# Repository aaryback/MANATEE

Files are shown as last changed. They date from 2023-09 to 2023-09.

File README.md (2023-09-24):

# "DIY" Emulsions using MANATEE (MANifold Adapter and Tray for Easy Emulsions)
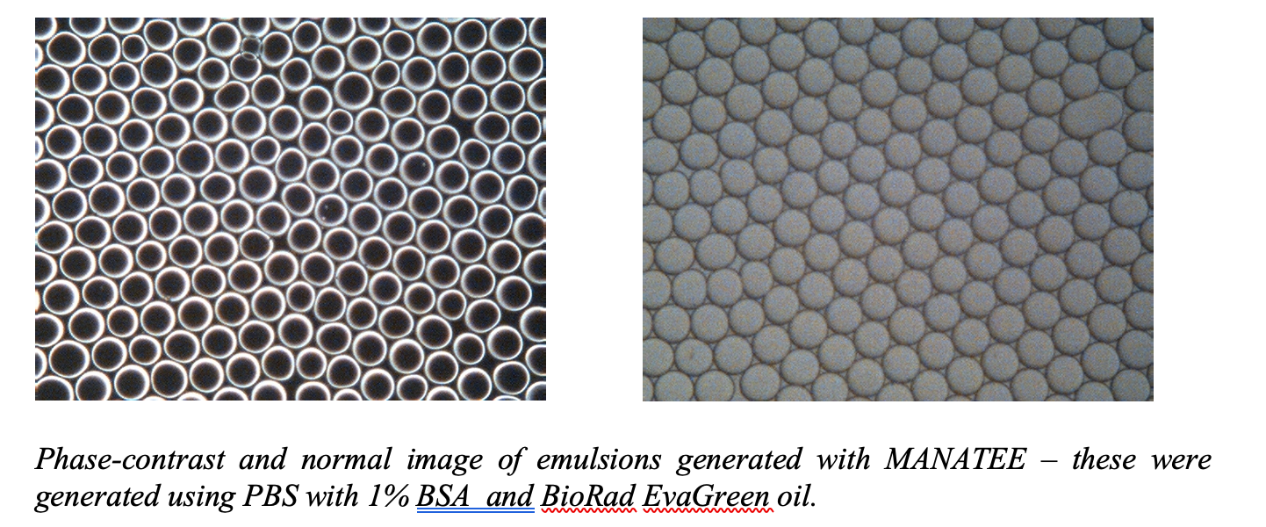
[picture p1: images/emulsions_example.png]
Example Emulsions


Here are instructions for making uniform emulsions using a 3D printed manifold attached to a generic vacuum source and a simple Arduino-controlled vacuum release system. 

The system uses commercially available QX200 microfluidics chips from BioRad QX200™ Droplet Digital™ PCR System and rubber gaskets, and the EvaGreen Droplet Generation Oil. It can save you buying the droplet generator if you want to just make emulsions - we weren’t interested in using it for digital droplet PCR so did not need the droplet reader either. This design could definitely be refined and improved, but as it stands it works just fine to make stable emulsions! If you have a very sensitive vacuum pump that can operate in the 5-15kPa range, then you can just attach that straight to the MANATEE and make your emulsions. We didn’t have that available, so instead made a ‘vacuum release’ circuit which can be attached to a generic vacuum source and then just releases the low level of vacuum needed to generate the emulsions.

## The MANATEE

The MANATEE manifold and tray were 3D printed using SLS with plastic polyamide 11: PA 11 plastic. 3D objects were uploaded to [Shapeways](https://www.shapeways.com/). and ordered for 3D printing. See “3D_objects” folder for the 3D printing files. SLS was chosen since extrusion-based 3D printing tends to have a slightly ribbed/uneven surface and to allow the wells on the microfluidics chip to be completely sealed off I wanted a super smooth finish. The tray could be printed using standard extrusion-based 3D printing though since its function is mainly to keep the rubber gasket and the microfluidics chip secured. The MANATEE was designed so that the Manifold can be clamped onto the tray with a vice (or similar) and even pressure applied.

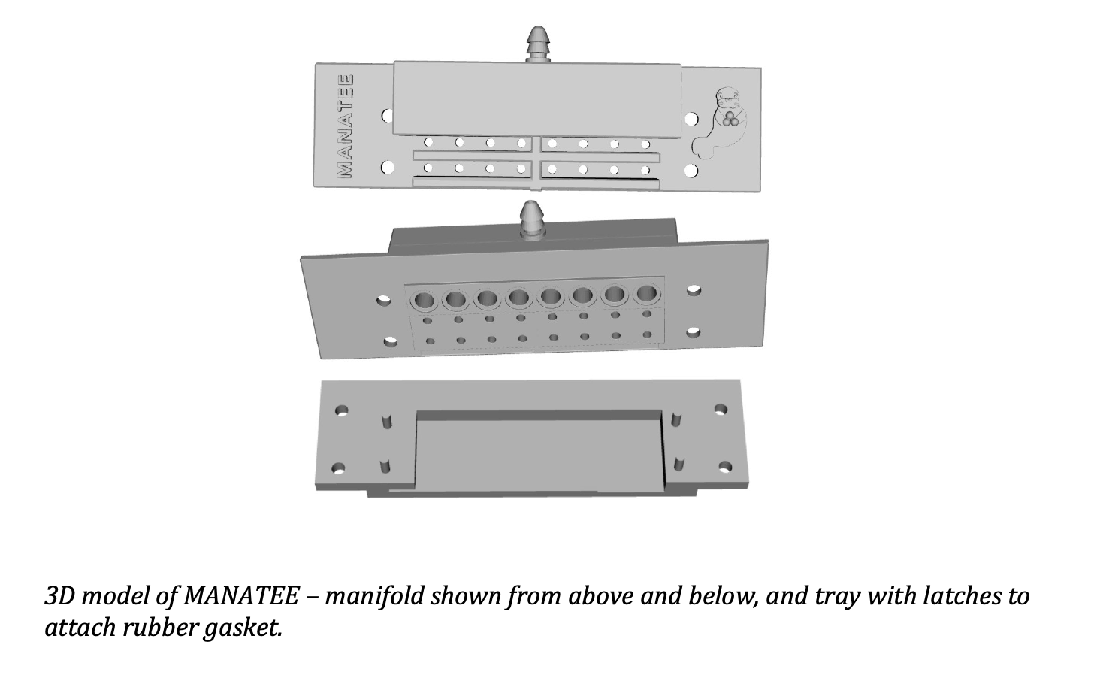
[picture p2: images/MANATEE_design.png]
MANATEE 3D design


3D model of MANATEE – manifold shown from above and below, and tray with latches to attach rubber gasket.

The microfluidics chip only slots into the tray in one orientation. The oil is added to the bottom well, the mastermix to the middle well and the emulsion is collected from the top well. The gasket is the strapped over the chip on the tray, fitting the holes on either end of the gasket over the latches. Then use a vice or similar to secure the manifold to the tray. I clamp both onto the workbench to ensure it is tightly sealed and no air enters the manifold while the droplets are being generated. Apply a vacuum (I’ve found 6-10kPa is generally the range needed for most PCR reagents, but it will depend on the viscosity of the aqueous solution) until all the oil is drawn through the chip. You can see the level of oil left within the wells, looking at the manifold side-on.

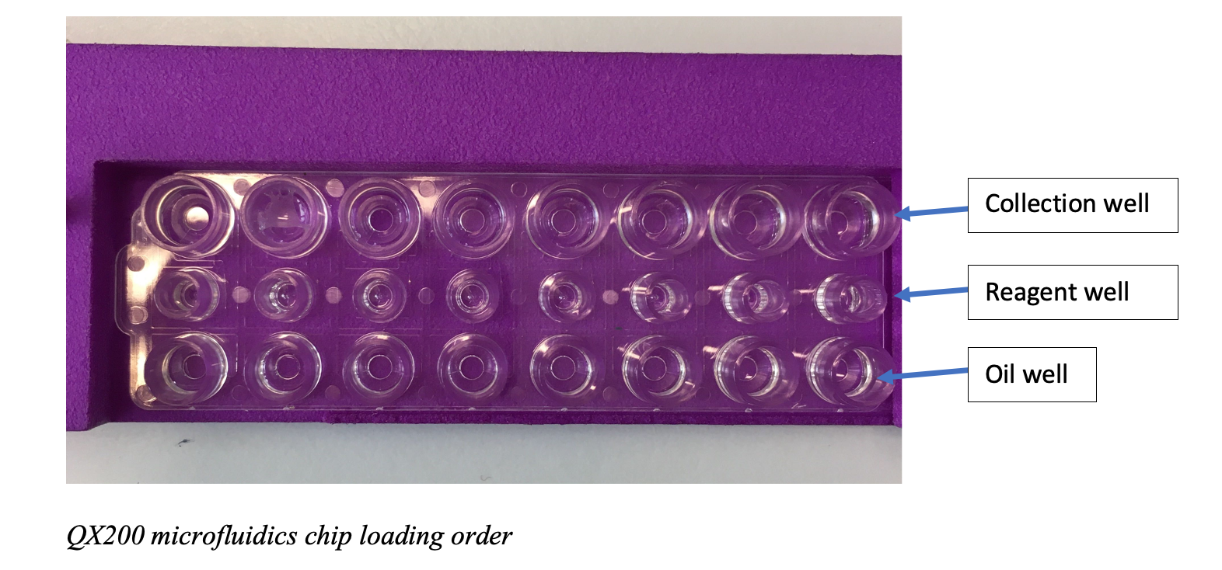
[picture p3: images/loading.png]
loading microfludics chip


## Vacuum Release System

If, like me, you don’t have access to a vacuum pump that can apply very low levels of vacuum required for microfluidics, you can also build this vacuum release system. When looking for precision vacuum pumps (that we were allowed to buy via the university) I was looking at having to spend several thousand pounds. So instead I just thought I’d use our existing crude vacuum pumps (e.g. ELISA plate washer) and release vacuum from there in a controlled manner. The whole thing probably cost around £50 to make (including the Arduino and tubing etc.), although I did already have some of the components (like the Duran bottle and ports for the Duran Bottle lid and some of the tubing). The expensive components are the Arduino and the pressure gauge. This circuit could be moved onto one of the really small Arduino circuit boards since you only need one digital and one analogue pin. The image below displays the overview of the main components in the setup:

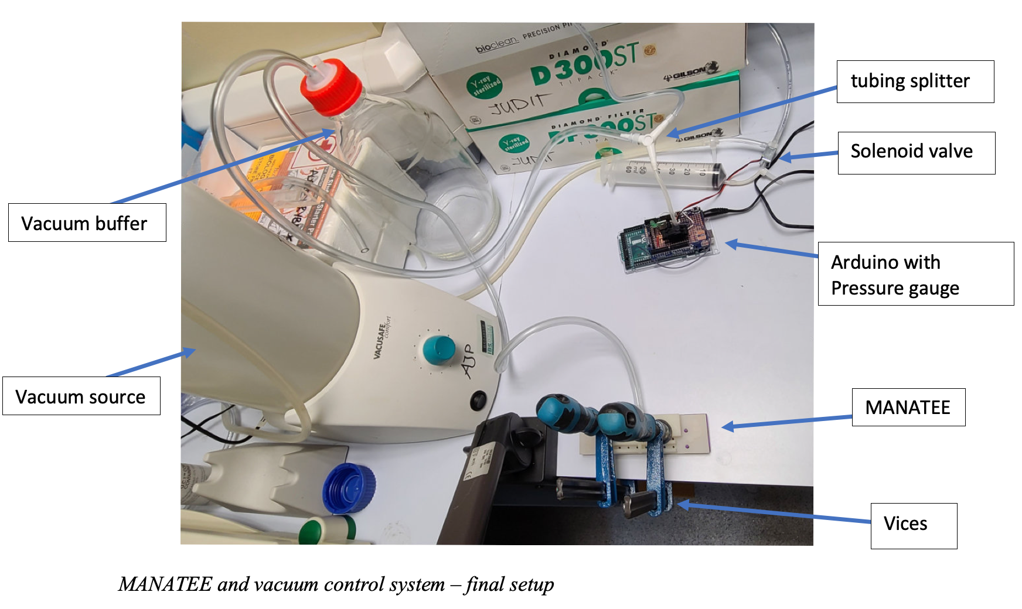
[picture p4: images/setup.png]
Droplet Generation Setup


Basically, the pressure gauge measures the vacuum in the system and if it is below the desired threshold, it briefly opens the solenoid valve to let more vacuum into the manifold, before closing off again. The circuit keeps opening and closing the solenoid valve to keep it roughly around the desired vacuum threshold. An LED light blinks each time more vacuum is released into the manifold, and as a way of making sure the circuit is working.

### A Brief Note on the Solenoid Valve:

I used a solenoid air valve, after considering quite a few different options this was the cheapest and simplest I could find (<£3). It can also easily be replaced since it plugs into the circuit rather than being soldered in. However, it does have three ports and switches between the central port (Port A) opening towards the lower plastic port (Port B), and the upper metal port (Port C). Because of this, I sealed Port B off so that vacuum accumulates in the plate-washer pump / tubing which is then released into the manifold. In the images, I just connected port B to a syringe with some tubing because this was the easiest “stopper” available to me but anything would work.

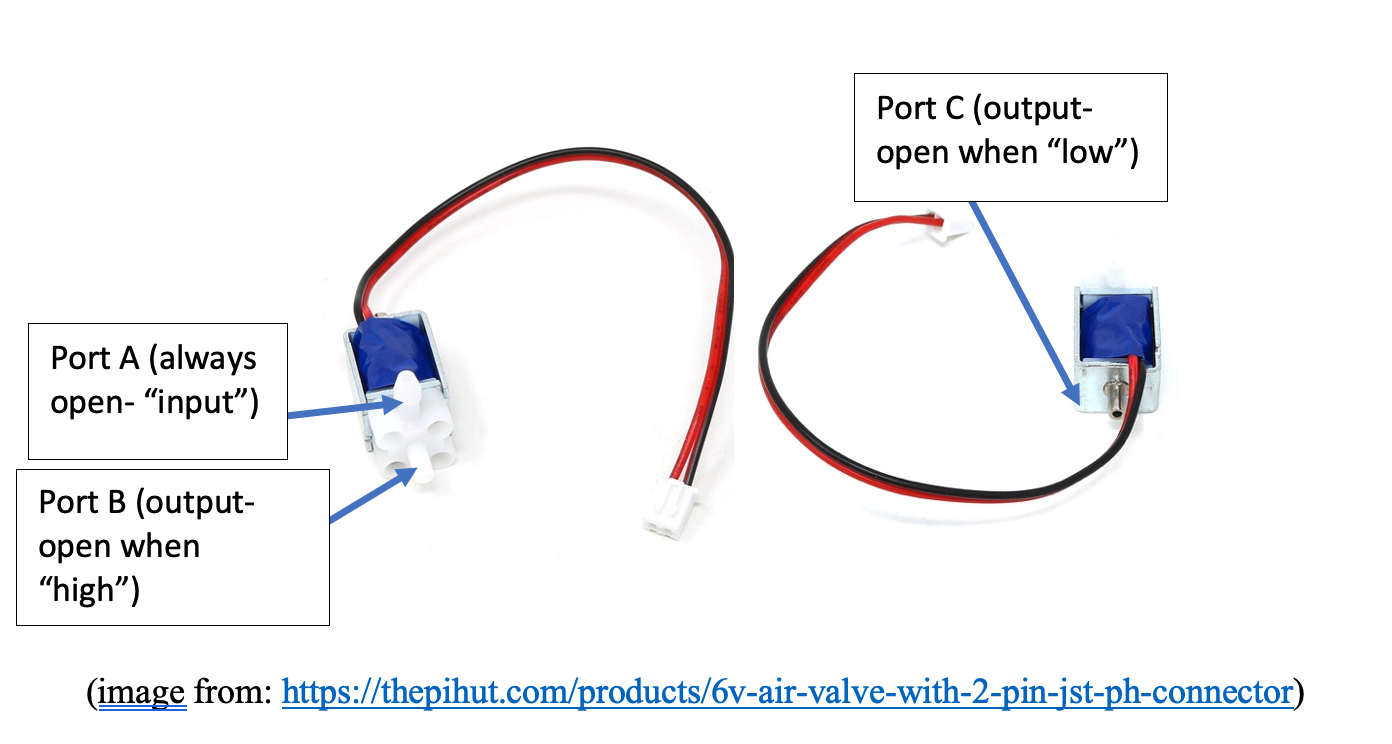
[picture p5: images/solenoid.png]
Solenoid valve


### Wiring up the Circuit:

Here are the details for the circuit (shown on a breadboard – in the final version this was soldered to an Arduino prototyping board):

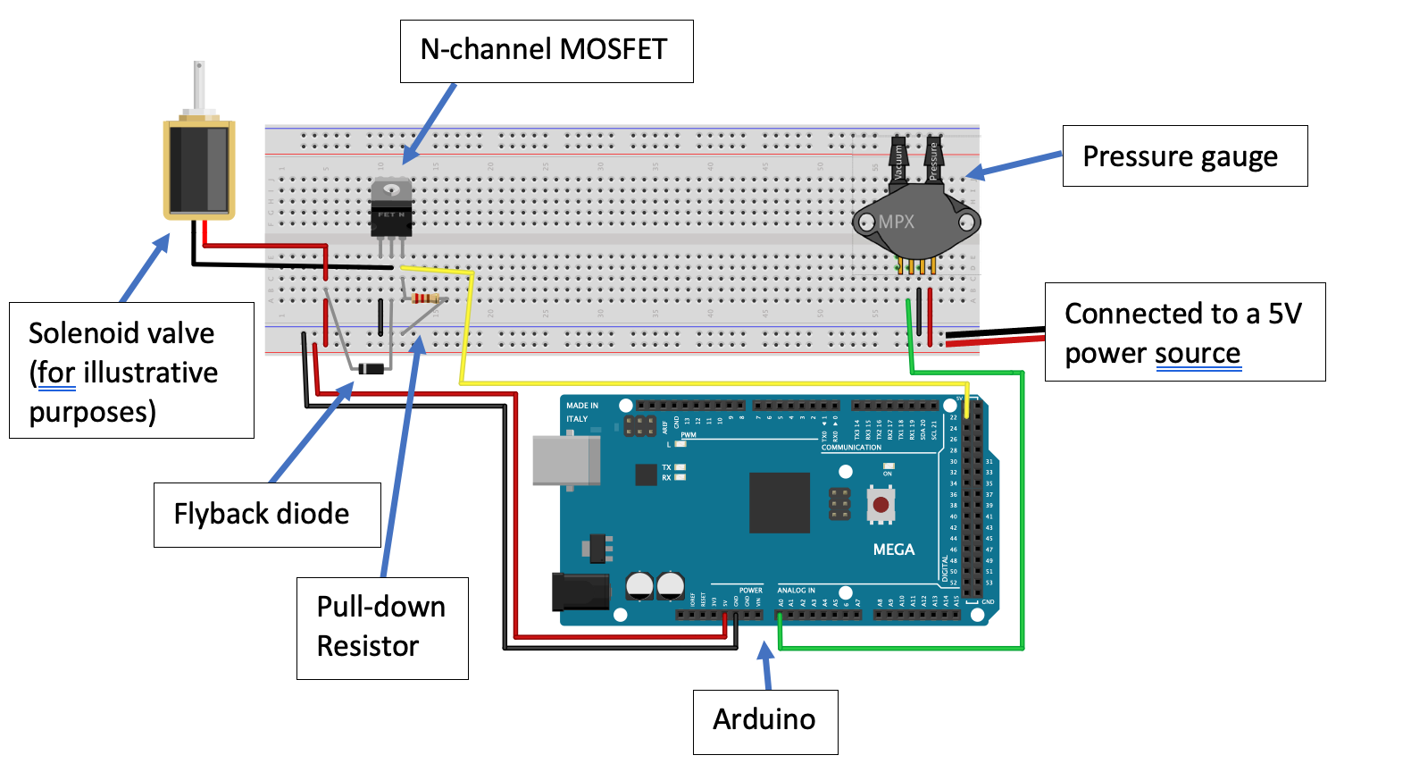
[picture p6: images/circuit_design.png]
Circuit


There are two main parts of the circuit: the pressure gauge and the solenoid. The pressure gauge is very simple:

I used an MPX5100 DP – a dual port differential pressure sensor (unlike the diagram it actually has 6 pins, but as in the diagram above, only the first three pins are used) which measures the difference in pressure between the two ports- one exposed to atmospheric pressure and the other one connected to the MANATEE.

In brief, the MPX5100 DP pressure gauge is connected to an Analog input pin on the Arduino (A0 here) and it is connected to power and ground. Code for pressure gauge was adapted from [here](https://circuits4you.com/2016/05/13/arduino-pressure-measurement/). As a quick sanity check that the calibration was correct, I checked the calibrated pressure against the observed output voltage and compared that to the manufacturer’s datasheet.

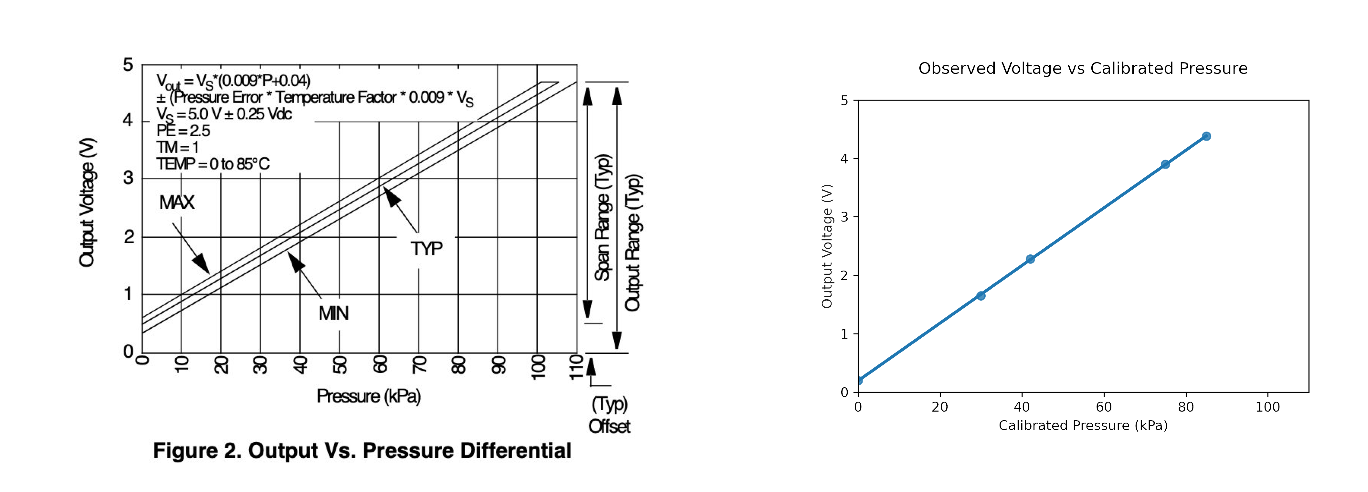
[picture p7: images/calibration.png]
Calibrating Pressure Gauge


Powering of the solenoid valve is controlled by a MOSFET, which in turn is controlled by the Arduino. The solenoid valve is connected to power directly but ground is connected to the middle pin of the N-Channel MOSFET. Pin 1 of the MOSFET connects to ground, pin 2 is the “output” connected to the solenoid and pin 3 is connected to the Arduino and to ground via a 220 ohm pull-down resistor. When the MOSFET receives a “HIGH” signal from the Arduino it opens the channel and powers the solenoid on, which blocks the airflow between the vacuum source and the MANATEE. When the MOSFET receives a “LOW” signal from the Arduino it powers the solenoid off and opens the airflow between the vacuum source and the MANATEE. A Flyback diode is included between the power and ground of the solenoid. If you want to include an LED to visually show whether the solenoid is powered on or off, you can include that between pin 3 of the MOSFET and the Digital pin 22 on the Arduino. 

The final Arduino code can be found in the folder [Arduino_Code](./Arduino_Code).

### Connecting the tubes:

I connected the tubing as follows: The vacuum source was connected to Port A of the solenoid valve. Port B of the solenoid is sealed off and not used. Port C of the solenoid valve feeds into a three way tube splitter with one port leading to a large Duran bottle to buffer the vacuum which also leads to the MANATEE, and the other port leading to the vacuum sensing port of the dual-port pressure gauge. This allows the vacuum in the manifold to be measured. 
To operate it, first turn on the vacuum release circuit, then the vacuum source.
Finally, it is worth mentioning that this system is pretty flexible: I’ve tried BioRad’s RT-PCR reagents and Roche Titan’s RT-PCR mastermix (with BSA added!) and gotten thermostable emulsions. Other PCR reagents work too, just titrate BSA and surfactant (I used a non-ionic plurionic surfactant) and try a range of vacuum levels. Some commercial PCR reagents produce emulsions that look OK initially but go “sticky” once thermocycled. I don’t know what additives in the mastermix make this happen, but I’d just recommend trying them out empirically and seeing what works.

| Part                       | Catalogue Numbers / Specifications                                   |
|----------------------------|---------------------------------------------------------------------|
| Arduino                    | Arduino Mega 2560                                                  |
| Pressure Gauge              | MPX5100DP                                                           |
| Solenoid Valve              | DFRobot 6V 2-Position 3-Way Air Valve for Arduino (DFR0866)        |
| N-channel Power MOSFET     | IRLB8721PbF                                                         |
| Flyback Diode              | Vishay (1N4007E354)                                                |
| Green LED                  | Kingbright2 V Green LED 5mm (L-53GD, RS Components)                |
| Resistors                  | 220 Ω Resistor (RS PRO)                                            |
| Prototyping PCB Board      | Arduino UNO R3 ProtoShield (483150)                                 |
| Plastic PVC Tubing         | - RS PRO Hose Pipe, PVC, 3mm ID, 6mm OD                            |
|                            | - 2.5mm inner diameter stretchable tubing (use tubing 2.5-3mm wide, depending on how you connect your vacuum source) |
| Y-tubing Splitter          | I used one compatible with tubes 2-6mm in diameter. This was quite helpful as I could stretch different sized tubes onto the same splitter. |
| Sealing Grease             |                                                                     |
| Cable Ties                 |                                                                     |

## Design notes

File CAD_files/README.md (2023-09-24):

This folder contains the CAD files for 3D printing the MANATEE Manifold and Tray. I've uploaded both the designs as ".stl" files. You can also find the design and project description on "Thingiverse" [here](https://www.thingiverse.com/thing:6174004).

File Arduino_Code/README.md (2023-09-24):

This Arduino code runs the pressure gauge code and solenoid. Sensor offset may need to be adjusted depending on your Arduino.

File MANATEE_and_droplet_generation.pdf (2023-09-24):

Audrey Ryback – August 2023

Home-made emulsions using MANATEE (MANifold Adapter and Tray for Easy Emulsions):

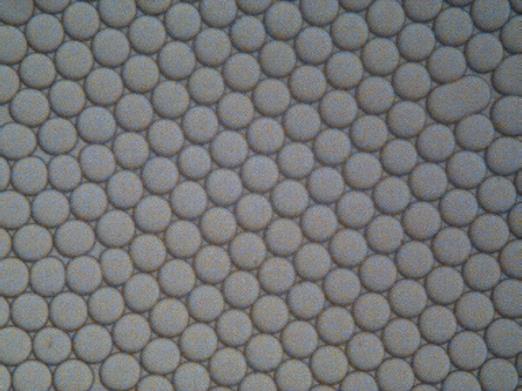
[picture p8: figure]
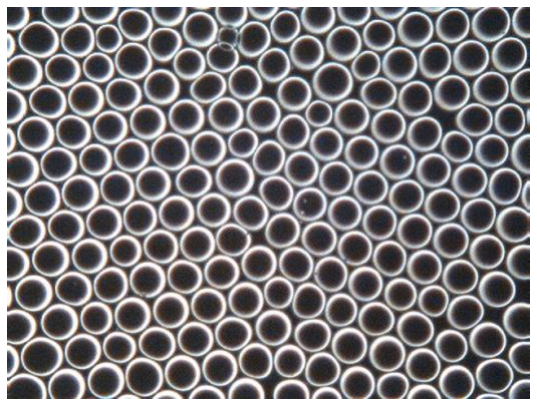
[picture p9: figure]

Phase-contrast and normal image of emulsions generated with MANATEE – these were generated using PBS with 1% BSA and BioRad EvaGreen oil.

Here are instructions for making uniform emulsions using a 3D printed manifold attached to a generic vacuum source and a simple Arduino-controlled vacuum release system. The system uses commercially available QX200 microfluidics chips from BioRad QX200™ Droplet Digital™ PCR System and rubber gaskets, and the EvaGreen Droplet Generation Oil. It can save you buying the droplet generator if you want to just make emulsions - we weren’t interested in using it for digital droplet PCR so did not need the droplet reader either. This design could definitely be refined and improved, but as it stands it works just fine to make stable emulsions! If you have a very sensitive vacuum pump that can operate in the 5-15kPa range, then you can just attach that straight to the MANATEE and make your emulsions. We didn’t have that available, so instead made a ‘vacuum release’ circuit which can be attached to a generic vacuum source and then just releases the low level of vacuum needed to generate the emulsions.

The MANATEE

The MANATEE manifold and tray were 3D printed using SLS with plastic polyamide 11: PA 11 plastic. 3D objects were uploaded to Shapeways (https://www.shapeways.com/) and ordered for 3D printing. See “3D_objects” folder for the 3D printing files. SLS was chosen since extrusion-based 3D printing tends to have a slightly ribbed/uneven surface and to allow the wells on the microfluidics chip to be completely sealed off I wanted a super smooth finish. The tray could be printed using standard extrusion-based 3D printing though since its function is mainly to keep the rubber gasket and the microfluidics chip secured. The MANATEE was designed so that the Manifold can be clamped onto the tray with a vice (or similar) and even pressure applied.

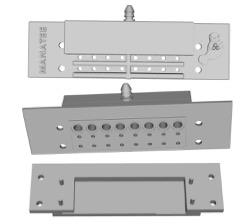
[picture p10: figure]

3D model of MANATEE – manifold shown from above and below, and tray with latches to attach rubber gasket.

The microfluidics chip only slots into the tray in one orientation. The oil is added to the bottom well, the mastermix to the middle well and the emulsion is collected from the top well.

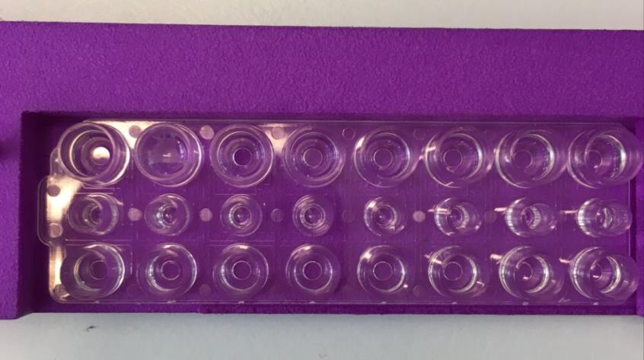
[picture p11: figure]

QX200 microfluidics chip loading order

The gasket is the strapped over the chip on the tray, fitting the holes on either end of the gasket over the latches.

Then use a vice or similar to secure the manifold to the tray. I clamp both onto the workbench to ensure it is tightly sealed and no air enters the manifold while the droplets are being generated. Apply a vacuum (I’ve found 6-10kPa is generally the range needed for most PCR

Oil well

Reagent well

Collection well reagents, but it will depend on the viscosity of the aqueous solution) until all the oil is drawn through the chip. You can see the level of oil left within the wells, looking at the manifold side-on.

Vacuum release system

If, like me, you don’t have access to a vacuum pump that can apply very low levels of vacuum required for microfluidics, you can also build this vacuum release system. When looking for precision vacuum pumps (that we were allowed to buy via the university) I was looking at having to spend several thousand pounds. So instead I just thought I’d use our existing crude vacuum pumps (e.g. ELISA plate washer) and release vacuum from there in a controlled manner. The whole thing probably cost around £50 to make (including the Arduino and tubing etc.), although I did already have some of the components (like the Duran bottle and ports for the Duran Bottle lid and some of the tubing). The expensive components are the Arduino and the pressure gauge. This circuit could be moved onto one of the really small Arduino circuit boards since you only need one digital and one analogue pin. The image below displays the overview of the main components in the setup:

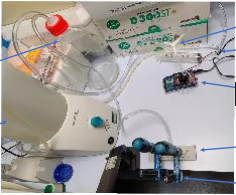
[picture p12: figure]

MANATEE and vacuum control system – final setup

Basically, the pressure gauge measures the vacuum in the system and if it is below the desired threshold, it briefly opens the solenoid valve to let more vacuum into the manifold, before closing off again. The circuit keeps opening and closing the solenoid valve to keep it roughly around the desired vacuum threshold. An LED light blinks each time more vacuum is released into the manifold, and as a way of making sure the circuit is working.

Arduino with
Pressure gauge

MANATEE

Vices

Vacuum source

Vacuum buffer

Solenoid valve

tubing splitter

A brief note on the solenoid valve:

I used a solenoid air valve, after considering quite a few different options this was the cheapest and simplest I could find (<£3). It can also easily be replaced since it plugs into the circuit rather than being soldered in. However, it does have three ports and switches between the central port (Port A) opening towards the lower plastic port (Port B), and the upper metal port (Port C). Because of this, I sealed Port B off so that vacuum accumulates in the plate-washer pump / tubing which is then released into the manifold. In the images, I just connected port B to a syringe with some tubing because this was the easiest “stopper” available to me but anything would work.

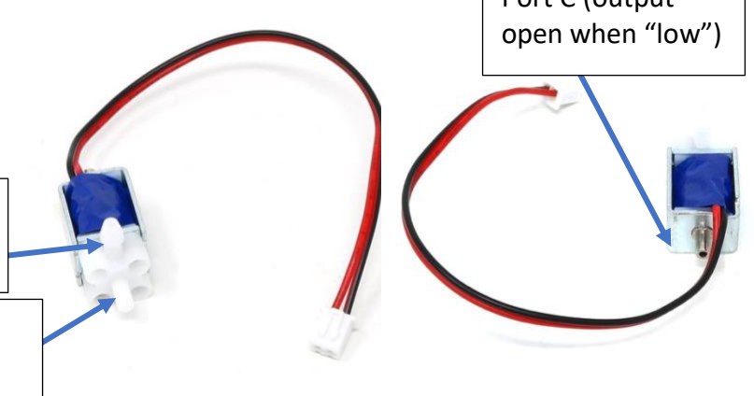
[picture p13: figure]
open when “low”)

(image from: https://thepihut.com/products/6v-air-valve-with-2-pin-jst-ph-connector)

Port A (always
open- “input”)

Port B (output-open when
“high”)

Port C (output-

Wiring up the circuit

Here are the details for the circuit (shown on a breadboard – in the final version this was soldered to an Arduino prototyping board):

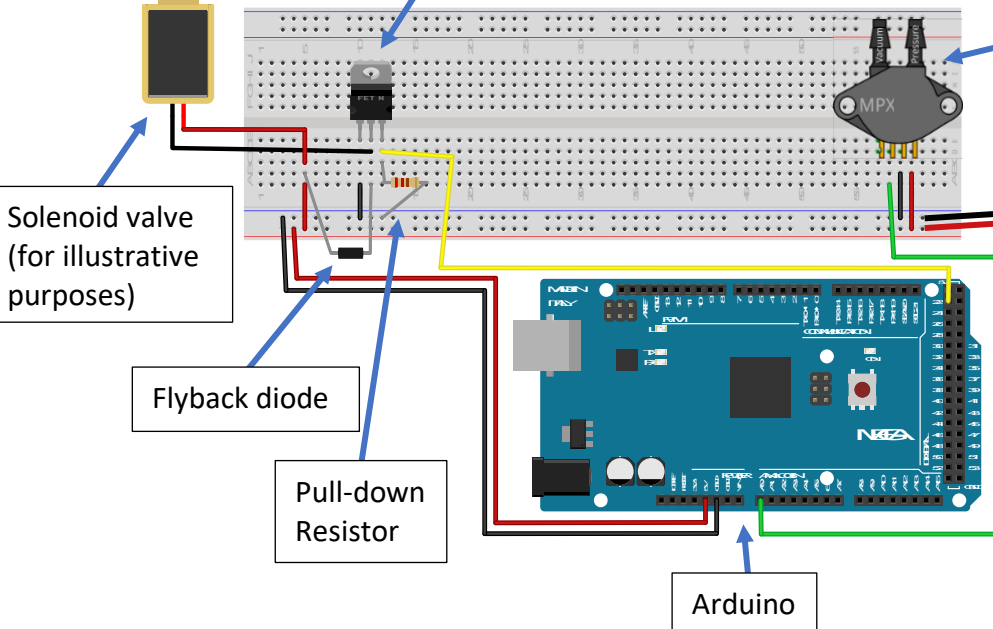
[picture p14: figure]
ANALOGIN; COMUNICATION; POWER; AREF; GND; RESET; VIN; SDA20; SCL21; MADEIN; ITALY; PWM; DIGITA; MEGA L; IOREF; Solenoid valve (for illustrative purposes); Flyback diode; Pull-down Resistor; Arduino

There are two main parts of the circuit: the pressure gauge and the solenoid. The pressure gauge is very simple:
I used an MPX5100 DP – a dual port differential pressure sensor (unlike the diagram it actually has 6 pins, but as in the diagram above, only the first three pins are used) which measures the difference in pressure between the two ports- on exposed to atmospheric pressure and the other one connected to the MANATEE.

In brief the MPX5100 DP pressure gauge is connected to an Anolog input pin on the Arduino (A0 here) and it is connected to power and ground. Code for pressure gauge was adapted from here: https://circuits4you.com/2016/05/13/arduino-pressure-measurement/ . As a quick sanity check that the calibration was correct, I checked the calibrated pressure against the observed output voltage and compared that to the manufacturer’s datasheet.

Pressure gauge

N-channel MOSFET

Connected to a 5V
power source

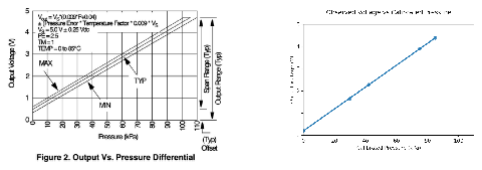
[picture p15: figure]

Powering of the solenoid valve is controlled by a MOSFET, which in turn is controlled by the Arduino. The solenoid valve is connected to power directly but ground is connected to the middle pin of the N-Channel MOSFET. Pin 1 of the MOSFET connects to ground, pin 2 is the “output” connected to the solenoid and pin 3 is connected to the Arduino and to ground via a 220 ohm pull-down resistor. When the MOSFET receives a “HIGH” signal from the Arduino it opens the channel and powers the solenoid on, which blocks the airflow between the vacuum source and the MANATEE. When the MOSFET receives a “LOW” signal from the Arduino it powers the solenoid off and opens the airflow between the vacuum source and the MANATEE. A Flyback diode is included between the power and ground of the solenoid. If you want to include an LED to visually show whether the solenoid is powered on or off, you can include that between pin 3 of the MOSFET and the Digital pin 22 on the Arduino.

The final Arduino code can be found in the folder “Arduino_code”.

Connecting the tubes:

I connected the tubing as follows: The vacuum source was connected to Port A of the solenoid valve. Port B of the solenoid is sealed off and not used. Port C of the solenoid valve feeds into a three way tube splitter with one port leading to a large Duran bottle to buffer the vacuum which also leads to the MANATEE, and the other port leading to the vacuum sensing port of the dual-port pressure gauge. This allows the vacuum in the manifold to be measured.

To operate it, first turn on the vacuum release circuit, then the vacuum source.

Finally, it is worth mentioning that this system is pretty flexible: I’ve tried BioRad’s RT-PCR reagents and Roche Titan’s RT-PCR mastermix (with BSA added!) and gotten thermostable emulsions. Other PCR reagents work too, just titrate BSA and surfactant (I used a non-ionic plurionic surfactant) and try a range of vacuum levels. Some commercial PCR reagents produce emulsions that look OK initially but go “sticky” once thermocycled. I don’t know what additives in the mastermix make this happen, but I’d just recommend trying them out empirically and seeing what works.

Materials:

Part | Catalogue Numbers / specifications
Arduino | Arduino Mega 2560
Pressure Gage | MPX5100DP
Solenoid Valve | DFRobot 6V 2-Position 3-Way Air Valve for Arduino (DFR0866)
N channel power MOSFET (30V 60A) | IRLB8721PbF
Flyback diode | Vishay (1N4007E354)
Green LED | Kingbright2 V Green LED 5mm (L-53GD, RS components)
Resistors | 220 Ω Resistor (RS PRO
Prototyping PCB board | Arduino UNO R3 ProtoShield (483150)
Plastic PVC tubing | - RS PRO Hose Pipe, PVC, 3mm ID, 6mm OD - 2.5mm inner diameter stretchable tubing (use tubing 2.5-3mm wide, depending on how you connect your vacuum source)
Y-tubing splitter | I used one which is compatible with tubes 2-6mm in diameter. This was quite helpful as I could stretch different sized tubes onto the same splitter.

Sealing grease

Cable ties

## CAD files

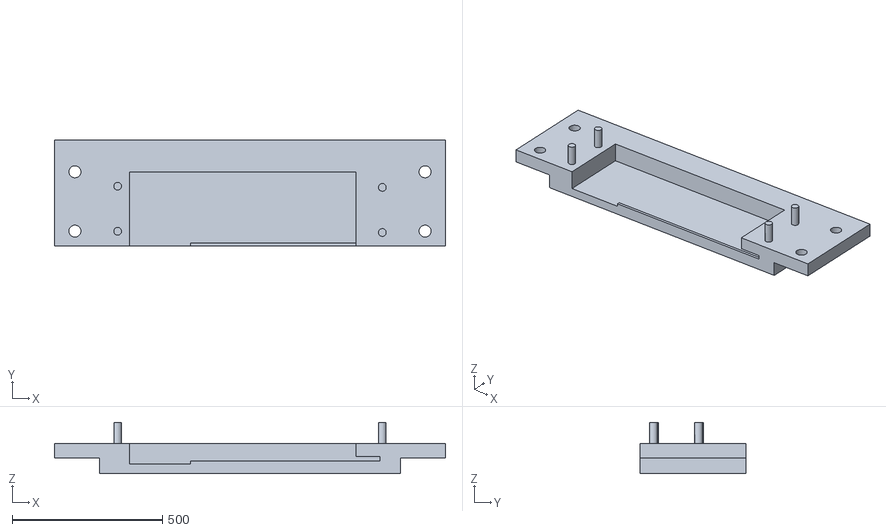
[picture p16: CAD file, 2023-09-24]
CAD_files/TRAY_MANATEE.stl
1300.0 x 354.0 x 170.0

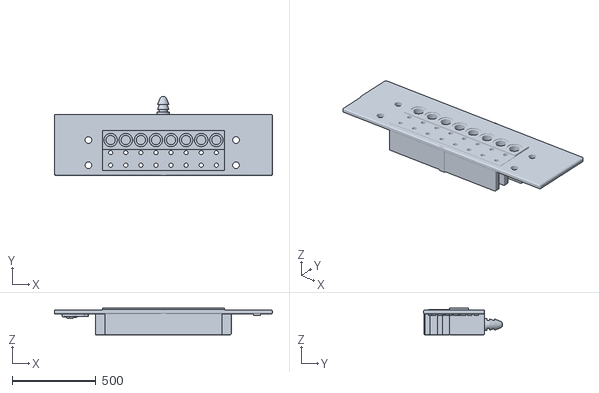
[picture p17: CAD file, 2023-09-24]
CAD_files/MANIFOLD_MANATEE.stl
1300.0 x 471.0 x 160.0

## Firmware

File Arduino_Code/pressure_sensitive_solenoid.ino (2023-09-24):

// ReadAnalogAverage
// Prints average to the serial monitor
// Typically the input is biased at Vcc/2 for a reading of ~512 with no signal
// Reads input A0

// sensor offset
const float SensorOffset = 38.0;
// digital pin 26 has a mosfet controlling a solenoid attached to it. Give it a name:
const int solenoid = 26;
const float pressure= 8.0;


// Global variables
int Analog;
float Sum;
float Average;

void setup() {
  // put your setup code here, to run once:
   Serial.begin(9600);
   pinMode(solenoid, OUTPUT);
   delay(100);       //"Stabilization time".   Probably not necessary
   Serial.print("Hiya, I'm a pressure sensor \n");

}

void loop() {
  // put your main code here, to run repeatedly:
Sum = 0;        //Initialize/reset

//Take 1000 readings, find min, max, and average.  This loop takes about 100ms.
for (int i = 0; i < 1000; i++)
{
  Analog = analogRead(A0);

  Sum = Sum + Analog;   //Sum for averaging     
}

Average = (Sum/1000);

//Calibration
float Average_calib= (Average-SensorOffset)/10.0;


if (Average_calib >= pressure) {
  delay(100);
  digitalWrite(solenoid,LOW);
// if the gauged pressure is higher than the pressure cutoff, send a LOW V signal to the mosfet (ie Valve closed!)
} else {
  delay(20);
  digitalWrite(solenoid,HIGH);
// if the gauged pressure is lower than the pressure cutoff, send a HIGH V signal to the mosfet (ie Valve open)
}

Serial.print (" Average = ");
Serial.println (Average_calib);
}

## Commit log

2023-09-24 Add files via upload
    arduino code
2023-09-24 Add files via upload
    added .stl files
    [MANIFOLD_MANATEE.stl, TRAY_MANATEE.stl]
